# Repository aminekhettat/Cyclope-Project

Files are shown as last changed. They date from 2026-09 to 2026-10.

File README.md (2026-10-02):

# Cyclope

**A street-crossing assistant for blind and visually impaired people.**

The white cane tells you where to put your foot. GPS tells you where to go.
At the kerb, nothing speaks. Cyclope addresses that exact moment: recognising a
crosswalk, reading the state of a pedestrian traffic light, and guiding by voice
to a spoken address.

Developed by **[Blind Systems](https://www.blindsystems.org)** together with
successive cohorts of embedded-systems engineering students.

---

## Table of contents

- [About the project](#about-the-project)
- [Three generations](#three-generations)
- [Generation 3 architecture](#generation-3-architecture)
- [Repository layout](#repository-layout)
- [Getting started](#getting-started)
- [The four work packages](#the-four-work-packages)
- [Contributing](#contributing)
- [License and contact](#license-and-contact)

---

## About the project

Existing assistive devices — OrCam MyEye, Envision Glasses, Aira, Be My Eyes —
read text, describe scenes and recognise objects. None of them answers the two
questions that come up at every street corner: **where exactly is the crosswalk,
and is the light green for me?**

Cyclope deliberately limits itself to that problem. It is narrow enough to be
solved properly, rather than half-solved inside a device that claims to do
everything.

The project has three goals:

1. **On-device detection** of crosswalks and pedestrian traffic lights, with
   immediate voice feedback.
2. **Pedestrian navigation** guided by voice, from a spoken address.
3. **Map contribution**: report unmapped crosswalks to OpenStreetMap, after the
   user confirms by voice.

Cyclope is a research and development project. **It is not a product for sale,
and it does not replace the white cane.**

---

## Three generations

| | Period | Worn hardware | Where the intelligence runs | Limitation hit |
|---|---|---|---|---|
| **GEN 1** | 2024-2025 | 3D-printed glasses + ESP32-CAM; Raspberry Pi and battery in a backpack | Raspberry Pi, locally | Bulk: a computer carried on the back, a cable running down the face |
| **GEN 2** | 2025-2026 | 3D-printed glasses, board and battery in a central compartment | Remote AI service, reached through the phone over 4G | Dependence on a paid API, several seconds of latency |
| **GEN 3** | in progress | Two small enclosures clipped onto the temples of ordinary glasses | The user's own phone, offline | — |

### Generation 1 — the computer in the backpack

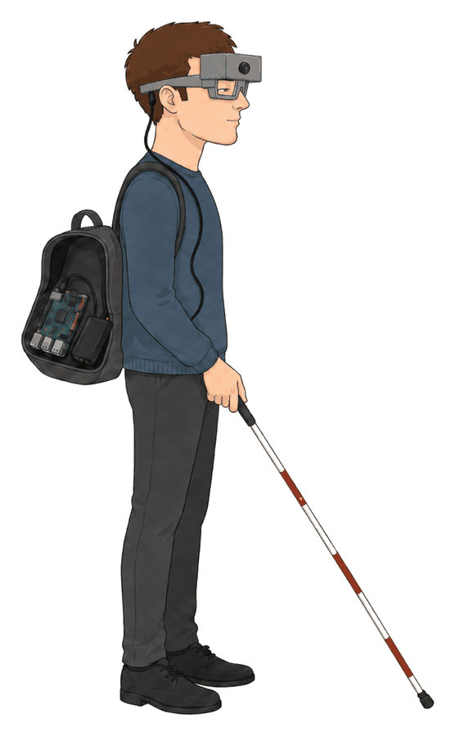
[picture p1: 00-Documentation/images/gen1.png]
Cartoon illustration of a blind man in profile holding a white cane. He wears bulky grey 3D-printed glasses with a large box on the forehead housing a camera. A black cable runs from the box down past his ear into an open backpack containing a green Raspberry Pi board and a battery.


An ESP32-CAM mounted on 3D-printed glasses streamed images over wifi to a
Raspberry Pi running the detection model. It worked — but the user had to carry a
computer and its battery on his back, with a cable hanging along his face.

### Generation 2 — the intelligence moved to the cloud

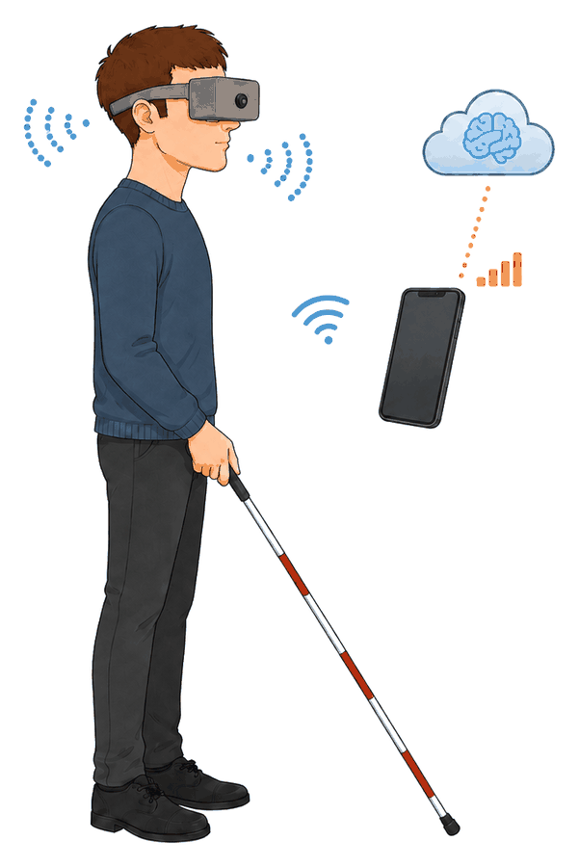
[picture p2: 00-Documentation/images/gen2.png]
Cartoon illustration of the same man. The backpack and cables are gone. A single 3D-printed box sits at the centre of the glasses frame, in front of the eyes. Blue wifi waves link the glasses to a smartphone; orange signal bars and a dotted line link the phone to a cloud symbol representing a remot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


The backpack disappeared: board and battery moved into a compartment built into
the glasses, and image analysis moved to a remote AI service reached through the
user's phone. Lighter to wear — but recognition now depended on a paid API and on
the mobile network, with several seconds of latency. Good enough to describe a
scene, not to warn in time.

### Generation 3 — computation moves back into the pocket

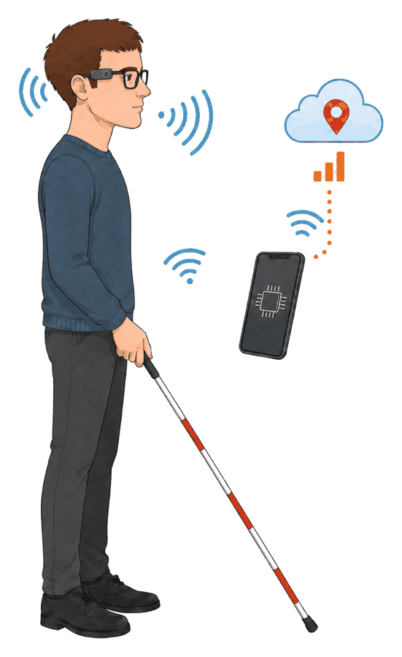
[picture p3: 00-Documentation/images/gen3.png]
Cartoon illustration of the same man wearing his own ordinary thin-framed glasses. A small industrial-looking module is clipped to each temple, joined by a thin cable running behind his head. Blue wifi waves link the module to a smartphone showing a processor chip icon; orange signal bars link the 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


The current version inverts the logic. The smartphone already in the user's
pocket becomes the brain: the detection model runs on it locally, offline and at
no cost. The network is only used for maps and addresses. On the hardware side we
stopped making glasses altogether — Cyclope is now a small module that clips onto
the user's own frames.

The common thread: **computation moves closer to the user, and cost tends
towards zero.**

Two lessons carried over from the previous generations:

- **We no longer build glasses.** Three runs of 3D-printed frames gave
  disappointing results in size, comfort and hinge robustness. GEN 3 clips onto
  the pair the person already chose.
- **We no longer depend on a remote AI for real-time detection.** Network latency
  is incompatible with an alert at the edge of a pavement.

---

## Generation 3 architecture

```
   Glasses module                  Android phone                   Internet
   ──────────────                  ─────────────                   ────────
   ESP32-S3 + camera   ── wifi ──▶  YOLO detection     ── 4G/5G ──▶  Nominatim
   2 buttons                        offline                          OSRM
   battery (2nd enclosure)          Voice feedback                   OpenStreetMap
                                    Navigation
```

- The **phone acts as the wifi access point**; the camera module connects to it
  as a client. No network setup is left to the user.
- **Visual detection runs offline**, on the phone.
- **Guidance requires an active data connection**: without internet, no address
  lookup and no route computation.
- **Voice feedback** is produced by the phone, which routes it to its own audio
  output (module speaker, wired or Bluetooth earphones).

GEN 3 hardware constraints: two enclosures joined by a USB-C cable running behind
the head, one holding the camera, the board and the buttons, the other the
battery, for balance. Mass target: **40 to 50 g**, with the OrCam MyEye 3 Pro
(22.5 g) as the market reference to keep in sight.

---

## Repository layout

This repository holds the whole project. It was assembled by merging the
historical per-topic repositories, **with full history and all branches
preserved**.

| Folder | Contents | Source repository |
|---|---|---|
| `00-Documentation/` | Cross-cutting documentation: meeting notes, specifications, reports | — |
| `01-Raspberry/` | GEN 1 server: stream reception, detection, recording | `Cyclope_Raspberry_Pi` |
| `02-Embedded/01-Software/` | ESP32 camera module firmware | `Cyclope_ESP32CAM` |
| `02-Embedded/02-Hardware/` | Schematic and PCB layout of the camera board | `Cyclope_ESP32CAM` |
| `03-Vision/` | YOLO model training, data augmentation, tests | `Cyclope_Vision` |
| `04-3D_Design/` | SolidWorks parts and STL files for the enclosures | `Cyclope-3D` |
| `05-MobilApp/` | Mobile applications: vision, navigation, voice feedback. `Android/` holds the current app, `iOS/` is reserved for a future port | `Cyclope_Androis` |

Folder numbering follows the chronological order of the project and fixes the
display order; it does not imply any dependency between work packages.

---

## Getting started

### Prerequisites per work package

| Package | Tools |
|---|---|
| `02-Embedded/01-Software` | ESP-IDF or Arduino IDE, ESP32-S3 board |
| `02-Embedded/02-Hardware` | **Altium Designer** (mandatory), parts verified as available at JLCPCB |
| `03-Vision` | Python 3.10+, Ultralytics, PyTorch |
| `04-3D_Design` | **SolidWorks** (mandatory) |
| `05-MobilApp/Android` | Android Studio, Kotlin, LiteRT |
| `05-MobilApp/iOS` | Xcode, Swift, Core ML - planned, not started |

### Clone

```bash
git clone https://github.com/ACCOUNT/Cyclope-Project.git
cd Cyclope-Project
```

### Train a detection model

```bash
cd 03-Vision
pip install -r requirements.txt      # create it if missing
python trainv11.py
```

### Large files: Git LFS

Model weights and CAD files are stored with **[Git LFS](https://git-lfs.com)**.
Install it once before cloning, otherwise those files arrive as small text
pointers instead of real content:

```bash
git lfs install
git clone https://github.com/ACCOUNT/Cyclope-Project.git
```

If you cloned before installing LFS, run `git lfs pull` to fetch the real files.

The following patterns are tracked, as recorded in the root `.gitattributes`:

```
*.pt  *.pth  *.onnx  *.tflite        model weights
*.STL  *.SLDPRT  *.SLDASM  *.SLDDRW  CAD parts and assemblies
```

Everything else — source code, documentation, images — stays in plain Git.

---

## The four work packages

GEN 3 is split into four independent subjects, each sized for **100 hours of one
student**. Every package can start immediately, without waiting for the others.

### 1. Electronics and enclosure — `02-Embedded/02-Hardware`, `04-3D_Design`

Adapt the existing GEN 2 schematic and redo the layout: replace the LDO with a
buck-boost converter, add at least two buttons, verify that every part is
available at JLCPCB. Design the two clip-on enclosures in SolidWorks. Assembly is
outsourced to JLCPCB: no soldering for the student. The ESP32-S3 is used as an
integrated module (antenna, SRAM, flash), which is out of scope for this project.

### 2. Embedded firmware — `02-Embedded/01-Software`

Image capture and compression, audio recording of voice commands (without
interpreting them), button handling, wifi link monitoring with a voice alert if
the connection drops.

### 3. Vision on Android — `05-MobilApp/Android`, `03-Vision`

Stream reception, on-device model inference, voice feedback. The student starts
with the already working DFRobot module from GEN 2, without waiting for the new
board.

### 4. Pedestrian navigation — `05-MobilApp/Android`

Spoken address input, geocoding through Nominatim, route computation, voice
guidance through TalkBack, positioning through the Fused Location and Fused
Orientation Providers. Includes the OpenStreetMap contribution feature. The
M5Stick C Plus serves as the button interface until the final module is ready.

---

## Contributing

### Branches

`main` is the reference branch and must always be in working order.

GEN 3 work takes place on the following branches, created from the current
`main` baseline. Each branch contains the complete repository; the work areas
below describe its purpose, not a restriction on which files can be edited.

| Branch | Work area |
|---|---|
| `CYCLOPE_GEN3_3D` | Clip-on enclosures, mechanical integration and SolidWorks files in `04-3D_Design/` |
| `CYCLOPE_GEN3_HW` | Schematics, PCB, power supply and buttons in `02-Embedded/02-Hardware/` |
| `CYCLOPE_GEN3_ESP32CAMSW` | ESP32-S3 camera firmware, audio capture, buttons and wifi in `02-Embedded/01-Software/` |
| `CYCLOPE_GEN3_AndroidVision` | Android stream reception, on-device detection and voice feedback in `05-MobilApp/Android/`, with model work in `03-Vision/` |
| `CYCLOPE_GEN3_AndroidNavigation` | Spoken destination, positioning, route guidance and OpenStreetMap contribution in `05-MobilApp/Android/` |

Collaborators may push commits to GEN 3 branches. Any additional work branch
must also start with `CYCLOPE_GEN3_`. Open a pull request to `main` when work is
ready for integration; the repository owner, `aminekhettat`, controls updates
to `main` and merges into it.

The historical branches (`android/…`, `design3d/…`, `embedded/…`, `raspberry/…`
and `vision/…`) are preserved as references. Collaborators cannot update or
delete them, or `main`. GitHub enforces this restriction on all branches outside
the `CYCLOPE_GEN3_` namespace, with bypass reserved to the repository admin.

The two Android branches share one application: coordinate interface changes
and integrate them through pull requests. The Raspberry Pi and future iOS port
have no dedicated GEN 3 work branch in the current scope.

### Commit messages

One imperative summary line, prefixed by the domain:

```
vision: add brightness-variation augmentation
embedded: fix wifi reconnection after access point loss
```

### Before pushing

- Never commit SolidWorks lock files (`~$…`), IDE settings (`.vs/`, `.idea/`) or
  build artefacts. The root `.gitignore` already excludes them.
- Large binary files must go through Git LFS. If you add a new binary type,
  register it first with `git lfs track "*.ext"` and commit the updated
  `.gitattributes` in the same change.

---

## License and contact

This project is released under the **Apache 2.0** license. See the `LICENSE` file.

- Website: [www.blindsystems.org](https://www.blindsystems.org)
- Contact: [contact@blindsystems.org](mailto:contact@blindsystems.org)

Field feedback — especially from blind and visually impaired users, occupational
therapists and orientation and mobility instructors — is what moves this project
forward the most.

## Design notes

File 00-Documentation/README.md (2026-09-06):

# Documentation

Cross-cutting documentation for the Cyclope project. One folder per work
package, mirroring the top-level layout of the repository.

| Folder | Holds |
|---|---|
| `Global/` | Documents covering the whole project: the presentation given to students, roadmaps, cross-package specifications |
| `01-Raspberry/` | Notes on the GEN 1 server |
| `02-Embedded/` | Meeting notes and specifications for the camera board and its firmware |
| `03-Vision/` | Dataset notes, training protocols, evaluation results |
| `04-3D_Design/` | Enclosure design notes, mass budget, print and assembly instructions |
| `05-MobilApp/` | Application specifications, accessibility notes, user-facing behaviour, one folder per platform |

`images/` holds the illustrations used by the root README.

Empty folders carry a `.gitkeep` file so that Git keeps them; delete it as
soon as the folder holds real content.

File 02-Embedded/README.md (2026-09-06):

# Cyclope_ESP32CAM
Repository that contain the PlatformIO project related to ESP32CAM modules management

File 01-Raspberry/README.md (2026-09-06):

# Cyclope_Raspberry_Pi
Repo that contains software development on Raspberry Pi that is used as a central calculation station

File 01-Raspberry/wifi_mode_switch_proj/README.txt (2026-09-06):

Voici comment installer et utiliser le script wifi_mode_switch.sh pour gérer le mode réseau de ton Raspberry Pi (mode Point d'accès ou mode Managed). 
Suis bien ces étapes :

Dans ton dossier de projet, tu devras avoir ces fichiers :

wifi_mode_switch.sh : Le script principal pour passer du mode AP au mode Managed.
hostapd.conf, dnsmasq.conf, dhcpcd.conf : Ces fichiers de configuration sont essentiels pour que le script fonctionne correctement.
install.sh : Un script qui copie automatiquement ces fichiers dans les répertoires système.

Il faudra également que tu modifies le fichier wpa_supplicant.conf ( je n'ai pas les droits pour le copier) qui se trouve dans /etc/wpa_supplicant.
Pour cela il faudra que tu tapes : 
sudo nano /etc/wpa_suppicant/wpa_supplicant.conf

et que tu rentres ces lignes de code : 

ctrl_interface=DIR=/var/run/wpa_supplicant GROUP=netdev
update_config=1

network={
    ssid="Nom_du_Réseau"   # Remplace par le SSID du réseau Wi-Fi
    psk="Mot_de_passe"      # Remplace par le mot de passe du réseau Wi-Fi
    key_mgmt=WPA2-PSK       # Utilise WPA2 pour la sécurité
}

Ouvre un terminal et va dans le dossier où tu as mis tous les fichiers (avec la commande cd). Ensuite, exécute le script install.sh en utilisant les droits administrateur pour que les fichiers de configuration soient copiés dans les bons répertoires système :

sudo ./install.sh
Ce script va :

Copier les fichiers de configuration (hostapd.conf, dnsmasq.conf, etc.) dans leurs répertoires respectifs sous /etc/.
Redémarrer les services nécessaires comme hostapd, dnsmasq, et dhcpcd pour appliquer la nouvelle configuration.

Une fois l’installation terminée, tu peux utiliser le script wifi_mode_switch.sh pour passer en mode Point d'accès ou Managed. Pour le faire, il suffit de passer l’argument approprié :

Pour passer en mode Point d'accès, lance cette commande :

sudo ./wifi_mode_switch.sh ap

Pour revenir en mode Managed, lance celle-ci :

sudo ./wifi_mode_switch.sh managed
Le script va automatiquement ajuster la configuration réseau de ton Raspberry Pi sans que tu aies à intervenir manuellement.

Si tu veux vérifier que ton Raspberry Pi est bien dans le mode que tu souhaites, tu peux utiliser des commandes comme ifconfig ou ip a pour voir l'état des interfaces réseau et leur configuration.

PS : Il se peut que lorsque tu exécutes la commande en mode AP, la raspberry reste en mode managed. Pour contrer cela, il te suffit de lancer la commande pour le mode managed et d'ensuite relancer la commande en AP.

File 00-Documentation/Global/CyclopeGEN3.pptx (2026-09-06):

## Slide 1

CyclopeGEN 3

Des lunettes qui disent où et quand traverser

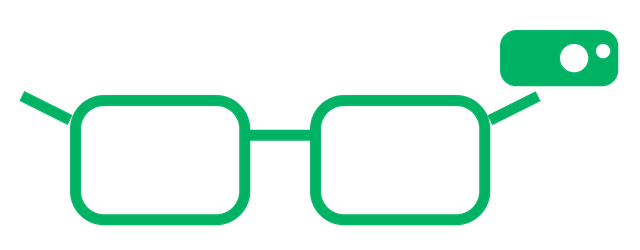
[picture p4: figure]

Projet longue durée · 5e année · Systèmes embarqués

Proposé par : Amine Khettat · BLIND SYSTEMS

E-mail : contact@blindsystems.org · www.blindsystems.org

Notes: 15 secondes. Une seule phrase : cette annee je vous propose la troisieme generation d'un projet qui tourne depuis deux ans, et cette annee c'est celle ou il devient portable.

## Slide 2

Le moment le plus dangereux est le moins outillé

La canne blanche dit où poser le pied.

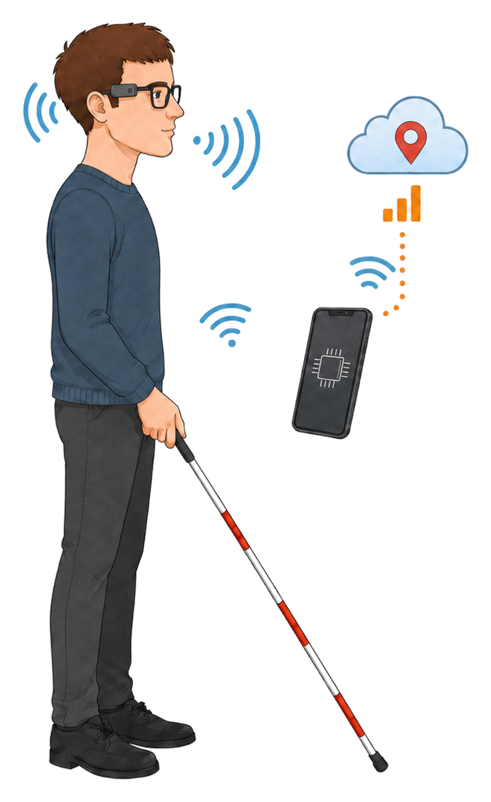
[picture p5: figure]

1

2

Le GPS dit où aller.

3

Rien, aujourd'hui, ne dit où ni quand traverser.

Cyclope regarde la rue et le dit à voix haute.

www.blindsystems.org · CyclopeGEN 3

2

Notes: 35 secondes. Insister sur le fait que traverser est le seul moment du trajet ou l'usager n'a aucune information. Ne pas parler d'obstacles : le sujet, c'est la traversee.

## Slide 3

1

GEN 1 — l'ordinateur dans le sac

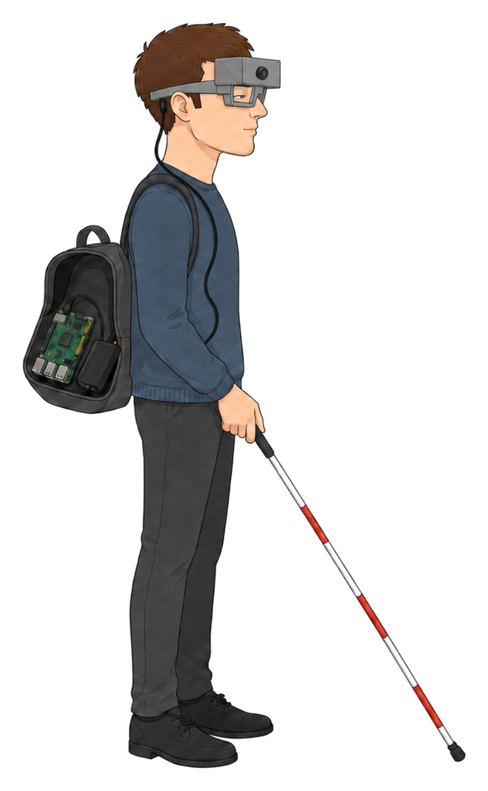
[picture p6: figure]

2024 – 2025

- Lunettes imprimées en 3D, branches non pliables, compartiment frontal abritant l'ESP32-CAM
- Câble d'alimentation apparent le long de l'oreille, jusqu'au sac à dos
- Raspberry Pi 5 et batterie dans le sac : flux MJPEG, YOLOv11, enregistrement vidéo
- Logique d'une caméra de sécurité que l'on porte sur soi

La limite

Des lunettes inconfortables, un câble qui pend, un sac à dos obligatoire.
Prototype lourd, non commercialisable.

Le calcul était dans un sac à dos. Il fallait l'en sortir.

www.blindsystems.org · CyclopeGEN 3

3

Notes: 30 secondes. La preuve de concept. Assumer l'echec franchement : c'est lui qui justifie la suite.

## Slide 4

2

GEN 2 — le serveur dans le cloud

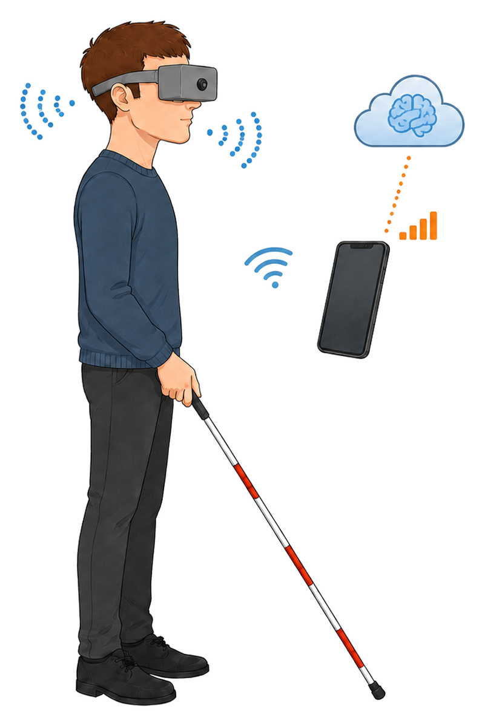
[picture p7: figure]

2025 – 2026

- Lunettes 3D avec un compartiment central devant les yeux : la carte et la batterie sont enfin embarquées
- Plus de Raspberry : l'ESP32 parle directement au téléphone, qui sert de point d'accès wifi
- Le téléphone relaie vers l'API d'OpenAI par sa 4G, et la scène est décrite à la voix
- En parallèle : carte DFRobot ESP32-S3, et conception de notre première carte maison

La limite

API payante, réseau obligatoire, quelques secondes de latence.
Le téléphone n'est qu'un relais : toute l'intelligence est ailleurs.

Le calcul était parti dans le cloud. Il fallait le rapatrier.

www.blindsystems.org · CyclopeGEN 3

4

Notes: 35 secondes. Le saut porte sur l'intelligence, pas sur le materiel. La limite de latence est ce qui amene GEN 3.

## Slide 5

3

GEN 3 — le téléphone déjà dans la poche

Module lunettes

Image, audio des commandes,
deux boutons

Téléphone

IA embarquée, hors ligne :
passages piétons, feux, couleur

Internet

Cartes et adresses seulement.
Aucune IA.

wifi local — le téléphone est le point d'accès

4G / 5G — sans données, pas de guidage

Deux boîtiers, un sur chaque branche

La batterie d'un côté, la caméra et la carte de l'autre, reliées par un fin câble d'alimentation : le poids est réparti et la monture reste en équilibre.
Cible 40 à 50 g — l'OrCam du marché en pèse 22,5.

On ne fabrique plus la lunette, on s'y accroche.

www.blindsystems.org · CyclopeGEN 3

5

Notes: 50 secondes. Deux messages : le calcul passe sur un telephone que l'usager a deja, et on arrete de fabriquer des lunettes. Preciser que la detection marche hors ligne, mais que le guidage exige une liaison de donnees. Les deux boitiers repondent au probleme d'equilibre de la monture. Insister : le telephone etait deja la en GEN 2, mais comme simple relais vers le cloud. En GEN 3 il devient le cerveau.

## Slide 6

Quatre briques, quatre élèves

Électronique et boîtiers

Adapter le schéma GEN 2, refaire le routage, buck-boost, deux boutons, et les deux boîtiers équilibrés sur les branches.

Altium · SolidWorks · JLCPCB

1

Firmware embarqué

Capture et compression d'image, enregistrement audio des commandes, gestion des appuis, surveillance du lien wifi.

ESP-IDF · C++ · ESP32-S3

2

Vision sur Android

Passages piétons, feux et leur couleur en temps réel, plus la description de scène à la demande, héritée de GEN 2.

YOLO · LiteRT · Kotlin

3

Navigation piétonne

Adresse dictée, itinéraire, guidage vocal, et contribution des passages manquants à OpenStreetMap.

Vosk · Nominatim · OSRM · TalkBack

4

Interfaces figées avant le démarrage, et un substitut pour chaque dépendance : personne n'attend personne.

www.blindsystems.org · CyclopeGEN 3

6

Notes: 80 secondes, la slide pivot. Une phrase par brique, pas plus. Terminer sur les substituts : la vision et le firmware demarrent sur les cartes DFRobot, la navigation sur le M5Stick. Aucun eleve n'est bloque par un autre.

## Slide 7

Le cadre

100 h

par élève

2

cartes prêtes à l'emploi

0

composant à braser

- Un dépôt git unique : une branche de travail par brique, modules Gradle séparés côté Android
- Matériel disponible dès la première séance, assemblage de la carte sous-traité
- Que du logiciel libre et gratuit, aucun abonnement
- Livrables : une démonstration qui fonctionne, et la documentation qui va avec

La démonstration de fin d'année est garantie : le système complet tourne déjà sur le matériel GEN 2.

www.blindsystems.org · CyclopeGEN 3

7

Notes: 25 secondes. Le message qui leve les freins : le materiel est la, rien a braser, et la demo finale ne depend pas de la nouvelle carte.

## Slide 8

Pourquoi celui-là

Un projet dont quelqu'un se servira vraiment

La chaîne complète : capteur, IA embarquée, utilisateur

Une démonstration que vous pourrez montrer, et garder

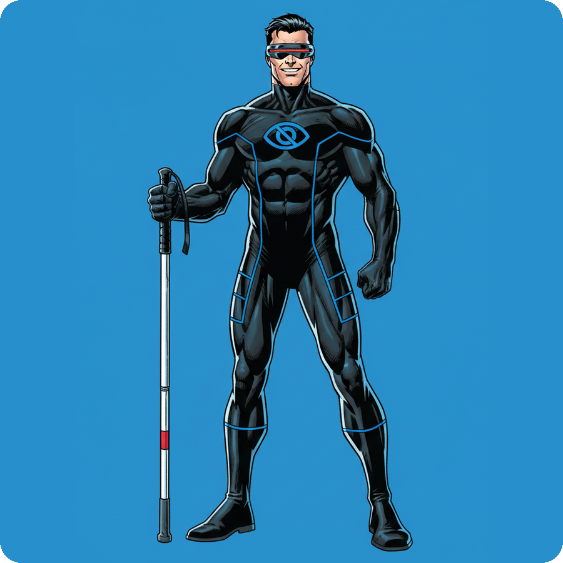
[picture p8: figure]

Venez me voir à la fin de la séance.

Proposé par : Amine Khettat · BLIND SYSTEMS

E-mail : contact@blindsystems.org · www.blindsystems.org

www.blindsystems.org · CyclopeGEN 3

8

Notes: 15 secondes. Terminer sur l'invitation, pas sur la technique.

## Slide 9

Annexe — jeux de données et versions de YOLO

Jeux de données utilisables directement

- CDSet / CDNet — passages piétons : 3 080 images d'entraînement, 1 770 de test, annotations déjà au format YOLO, deux classes (passage, flèche au sol)
- PTL / ImVisible — feux piétons : 5 059 images, cinq classes dont vert avec décompte, licence MIT ; le réseau LytNet tourne à 21 images/s sur un iPhone 7
- Ampel-Pilot — feux piétons allemands : 3 696 images, 4 311 annotations, licence MIT, collecté pour une application destinée aux malvoyants
- Et le jeu de données Cyclope 2024-2025, déjà constitué et augmenté par la promotion GEN 1

Attention : Bosch, LISA et DriveU sont des jeux de feux véhicules vus depuis une voiture. Cyclope a besoin de feux piétons vus du trottoir — autre objet, autre point de vue.

Versions de YOLO

- YOLOv5 : celui de CDNet, le seul si l'on veut réutiliser des poids existants tels quels — YOLOv8 puis YOLO11, celui déjà entraîné en GEN 1 : écosystème mature
- YOLO26 (janvier 2026) : inférence sans NMS, donc plus de post-traitement à réimplémenter sur mobile, environ 43 % plus rapide sur CPU, export LiteRT
- Licence AGPL-3.0 pour tous les modèles Ultralytics ; YOLOX est en Apache 2.0 si une exploitation commerciale est envisagée un jour

www.blindsystems.org · CyclopeGEN 3

9

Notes: Annexe, hors chrono. A sortir si un eleve demande sur quoi il va entrainer son modele.

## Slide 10

Annexe — le contrat d'interface

Le sens de la liaison wifi

Le téléphone active son point d'accès, le module s'y connecte. La 4G reste la route internet du téléphone : aucun conflit de réseau.

Ce que porte le protocole

Trames JPEG, audio des commandes vocales, événements bouton, état du lien. Figé avant le démarrage, identique pour le M5Stick et pour la carte finale.

Le retour vocal

L'application envoie une commande de lecture au téléphone, qui route vers sa sortie — haut-parleur, écouteurs filaires ou Bluetooth. Hors périmètre du projet.

Deux liens surveillés, deux alertes

Le firmware surveille le wifi et alerte sur son propre haut-parleur, seul cas où le téléphone ne peut plus parler. L'application surveille la liaison de données.

Les substituts

Vision et firmware démarrent sur les deux cartes DFRobot de GEN 2, la navigation sur le M5Stick C Plus, lui aussi en wifi. Aucune brique n'attend une autre.

Question ouverte à traiter dès la conception : comment le module apprend-il le nom et le mot de passe du point d'accès, sans écran ni clavier ?

www.blindsystems.org · CyclopeGEN 3

10

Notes: Annexe, hors chrono. A sortir si un eleve demande comment les briques communiquent.

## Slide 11

Annexe — l'état de l'art

Un boîtier qui se clipse sur la monture de lunettes. Lit le texte à voix haute, reconnaît visages et objets, traitement embarqué. C'est notre référence de format et de poids.

OrCam MyEye

Envision Glasses

Des lunettes connectées : lecture de texte, description de scène, appel à un proche voyant. Orientées lecture et reconnaissance.

eSight

Des lunettes à écrans internes qui amplifient et retraitent l'image. Conçues pour la vision résiduelle, donc pas pour les non-voyants.

Aira

Un service d'agents humains formés, joignables depuis l'application, qui décrivent la scène en direct par la caméra. Sur abonnement.

Be My Eyes

Une application gratuite qui met en relation avec des bénévoles voyants, doublée d'une description automatique par IA.

Rango, de GoSense

Un boîtier français qui se clipse sur la canne blanche : détection d'obstacles et guidage sonore, avec dictée d'adresse. Le plus proche de nous.

Aucun des six ne traite la traversée de rue : ni où traverser, ni quand. C'est précisément là que Cyclope se place.

www.blindsystems.org · CyclopeGEN 3

11

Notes: Annexe, hors chrono. Le benchmark vient du rapport GEN 1. Le point a retenir : tous lisent du texte ou decrivent une scene, aucun ne repond a la question de la traversee.

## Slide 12

Annexe — références

- CDSet, jeu de données passages piétons — zenodo.org/records/8289874
- CDNet, détection de passages piétons temps réel — github.com/zhangzhengde0225/CDNet
- ImVisible et LytNet, feux piétons pour malvoyants — github.com/samuelyu2002/ImVisible
- Ampel-Pilot, feux piétons allemands — github.com/patVlnta/Ampel-Pilot-Dataset
- Ultralytics YOLO26 — docs.ultralytics.com/models/yolo26
- monicz.dev — cartographie automatique de passages piétons sur OpenStreetMap
- OrCam MyEye 3 Pro — 22,5 g, 76 × 21 × 14,9 mm, fixation magnétique sur la branche
- Rango, de GoSense (Lyon) — la référence française du guidage pour non-voyants

www.blindsystems.org · CyclopeGEN 3

12

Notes: Annexe, hors chrono.

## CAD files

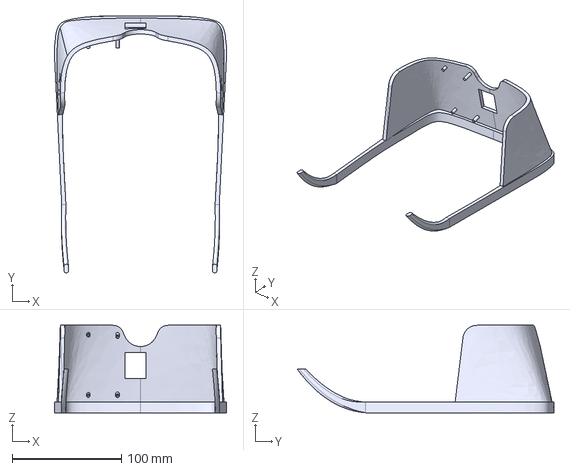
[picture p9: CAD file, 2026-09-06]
02-Embedded/02-Hardware/Glasses_ISMAIL.step
157.3 x 234.9 x 80.0 mm

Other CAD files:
04-3D_Design/Assemblage_lunettes - Lunettes-1.STL
04-3D_Design/Assemblage_lunettes - Boitier-2.STL
04-3D_Design/Assemblage_lunettes.SLDASM
04-3D_Design/Lunettes.SLDPRT
04-3D_Design/Boitier.SLDPRT

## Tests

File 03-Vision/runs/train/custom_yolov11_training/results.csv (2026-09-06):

epoch | time | train/box_loss | train/cls_loss | train/dfl_loss | metrics/precision(B) | metrics/recall(B) | metrics/mAP50(B) | metrics/mAP50-95(B) | val/box_loss | val/cls_loss | val/dfl_loss | lr/pg0 | lr/pg1 | lr/pg2
1 | 111.023 | 1.40003 | 2.88625 | 1.55938 | 0.51152 | 0.40126 | 0.38823 | 0.22607 | 1.52438 | 1.95877 | 1.66085 | 0.00033223 | 0.00033223 | 0.00033223
2 | 226.436 | 1.35667 | 1.93575 | 1.5003 | 0.5898 | 0.48392 | 0.46685 | 0.26641 | 1.55463 | 1.6891 | 1.64722 | 0.000652385 | 0.000652385 | 0.000652385
3 | 339.31 | 1.32899 | 1.60861 | 1.46598 | 0.57497 | 0.4881 | 0.49652 | 0.27497 | 1.63236 | 1.5564 | 1.78132 | 0.00095934 | 0.00095934 | 0.00095934
4 | 452.086 | 1.31024 | 1.44595 | 1.44707 | 0.68048 | 0.53559 | 0.5746 | 0.32416 | 1.55523 | 1.44 | 1.62224 | 0.0009406 | 0.0009406 | 0.0009406
5 | 572.982 | 1.25822 | 1.31063 | 1.40136 | 0.69185 | 0.52315 | 0.55078 | 0.34459 | 1.38886 | 1.31957 | 1.51859 | 0.0009208 | 0.0009208 | 0.0009208
6 | 694.308 | 1.22613 | 1.2392 | 1.37718 | 0.72523 | 0.57857 | 0.60999 | 0.36042 | 1.42285 | 1.2142 | 1.52768 | 0.000901 | 0.000901 | 0.000901
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

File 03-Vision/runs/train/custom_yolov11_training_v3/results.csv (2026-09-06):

epoch | time | train/box_loss | train/cls_loss | train/dfl_loss | metrics/precision(B) | metrics/recall(B) | metrics/mAP50(B) | metrics/mAP50-95(B) | val/box_loss | val/cls_loss | val/dfl_loss | lr/pg0 | lr/pg1 | lr/pg2
1 | 175.57 | 1.30136 | 2.04895 | 1.51353 | 0.63001 | 0.55663 | 0.5529 | 0.34393 | 1.40303 | 1.48832 | 1.51691 | 0.0033223 | 0.0033223 | 0.0033223
2 | 356.928 | 1.2394 | 1.30434 | 1.42803 | 0.68141 | 0.51924 | 0.57533 | 0.3374 | 1.48535 | 1.28497 | 1.66132 | 0.00663916 | 0.00663916 | 0.00663916
3 | 536.09 | 1.2954 | 1.29864 | 1.45799 | 0.66905 | 0.55345 | 0.57695 | 0.35933 | 1.40399 | 1.59334 | 1.62224 | 0.00993952 | 0.00993952 | 0.00993952
4 | 714.9 | 1.33262 | 1.31706 | 1.47529 | 0.70626 | 0.54789 | 0.58106 | 0.3503 | 1.42574 | 1.39348 | 1.62697 | 0.00992575 | 0.00992575 | 0.00992575
5 | 893.806 | 1.2869 | 1.21493 | 1.44021 | 0.82373 | 0.56077 | 0.64449 | 0.38767 | 1.42394 | 1.28836 | 1.54035 | 0.009901 | 0.009901 | 0.009901
6 | 1072.63 | 1.24432 | 1.15244 | 1.40564 | 0.82418 | 0.58405 | 0.66179 | 0.41749 | 1.2629 | 1.1314 | 1.44526 | 0.00987625 | 0.00987625 | 0.00987625
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

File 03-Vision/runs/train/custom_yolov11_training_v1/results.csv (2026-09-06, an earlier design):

epoch | time | train/box_loss | train/cls_loss | train/dfl_loss | metrics/precision(B) | metrics/recall(B) | metrics/mAP50(B) | metrics/mAP50-95(B) | val/box_loss | val/cls_loss | val/dfl_loss | lr/pg0 | lr/pg1 | lr/pg2
1 | 106.874 | 1.39041 | 3.20715 | 1.55206 | 0.37403 | 0.33083 | 0.33184 | 0.19432 | 1.51314 | 2.13887 | 1.57352 | 0.0033223 | 0.0033223 | 0.0033223
2 | 211.66 | 1.36292 | 2.19266 | 1.49892 | 0.59674 | 0.42867 | 0.45815 | 0.27465 | 1.45736 | 1.84805 | 1.58135 | 0.00663916 | 0.00663916 | 0.00663916
3 | 317.653 | 1.3674 | 1.88557 | 1.4937 | 0.5968 | 0.44064 | 0.45027 | 0.24702 | 1.65117 | 1.74711 | 1.77154 | 0.00993952 | 0.00993952 | 0.00993952
4 | 423.304 | 1.40957 | 1.7112 | 1.52288 | 0.64386 | 0.49048 | 0.50128 | 0.28947 | 1.51609 | 1.53231 | 1.66534 | 0.00992575 | 0.00992575 | 0.00992575
5 | 529.312 | 1.36471 | 1.51135 | 1.47739 | 0.76575 | 0.50121 | 0.57192 | 0.32437 | 1.49757 | 1.45249 | 1.60595 | 0.009901 | 0.009901 | 0.009901
6 | 636.017 | 1.33 | 1.40148 | 1.45757 | 0.68481 | 0.528 | 0.5604 | 0.33133 | 1.48398 | 1.38946 | 1.61082 | 0.00987625 | 0.00987625 | 0.00987625
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

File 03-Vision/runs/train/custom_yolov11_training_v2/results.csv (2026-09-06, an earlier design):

epoch | time | train/box_loss | train/cls_loss | train/dfl_loss | metrics/precision(B) | metrics/recall(B) | metrics/mAP50(B) | metrics/mAP50-95(B) | val/box_loss | val/cls_loss | val/dfl_loss | lr/pg0 | lr/pg1 | lr/pg2
1 | 123.104 | 1.34903 | 2.2515 | 1.53528 | 0.59989 | 0.48032 | 0.50617 | 0.30305 | 1.4329 | 1.32398 | 1.54411 | 0.0033223 | 0.0033223 | 0.0033223
2 | 249.056 | 1.25739 | 1.33016 | 1.4187 | 0.64755 | 0.50792 | 0.56872 | 0.35444 | 1.36075 | 1.39602 | 1.45911 | 0.00663916 | 0.00663916 | 0.00663916
3 | 378.102 | 1.30145 | 1.2859 | 1.43846 | 0.56419 | 0.53386 | 0.52213 | 0.30159 | 1.46114 | 1.43889 | 1.65279 | 0.00993952 | 0.00993952 | 0.00993952
4 | 507.061 | 1.34837 | 1.31839 | 1.46878 | 0.6467 | 0.53136 | 0.54582 | 0.3342 | 1.49357 | 1.46021 | 1.65333 | 0.00992575 | 0.00992575 | 0.00992575
5 | 636.223 | 1.30388 | 1.24159 | 1.42851 | 0.69306 | 0.53522 | 0.56421 | 0.32341 | 1.49617 | 1.36799 | 1.5882 | 0.009901 | 0.009901 | 0.009901
6 | 766.093 | 1.2745 | 1.16205 | 1.40862 | 0.73019 | 0.57636 | 0.61628 | 0.37205 | 1.36011 | 1.23116 | 1.51743 | 0.00987625 | 0.00987625 | 0.00987625
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

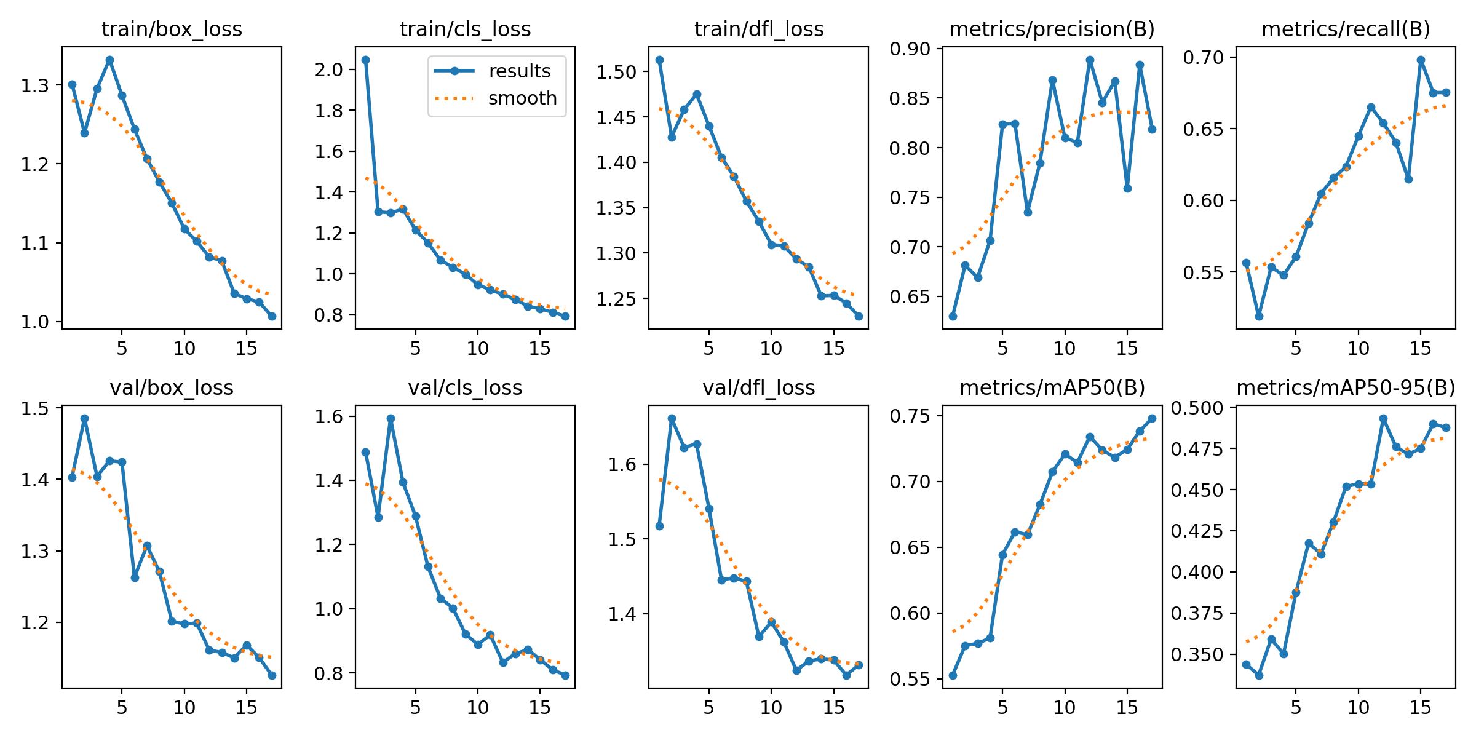
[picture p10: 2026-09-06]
03-Vision/runs/train/custom_yolov11_training_v3/results.png

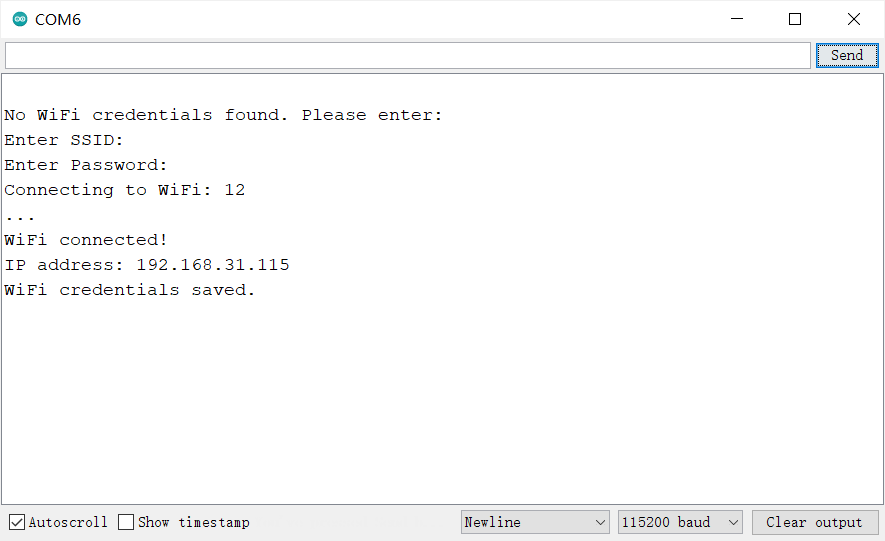
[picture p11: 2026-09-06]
02-Embedded/01-Software/ESP32Cam/PCB_firmware/CameraWebServer/Result.png

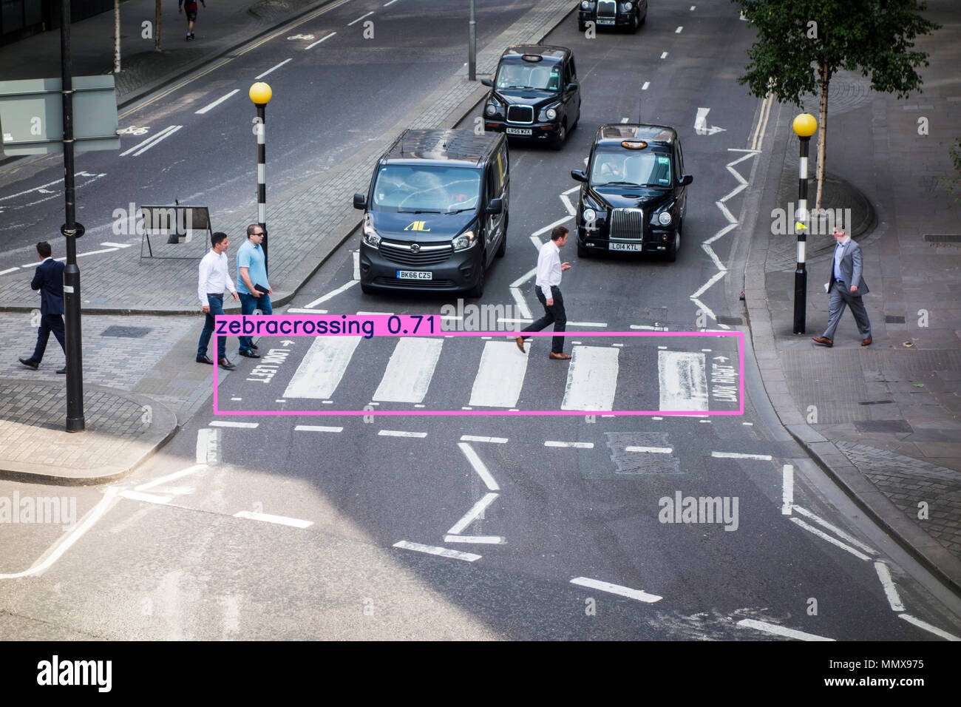
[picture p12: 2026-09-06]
03-Vision/result_initial.jpg

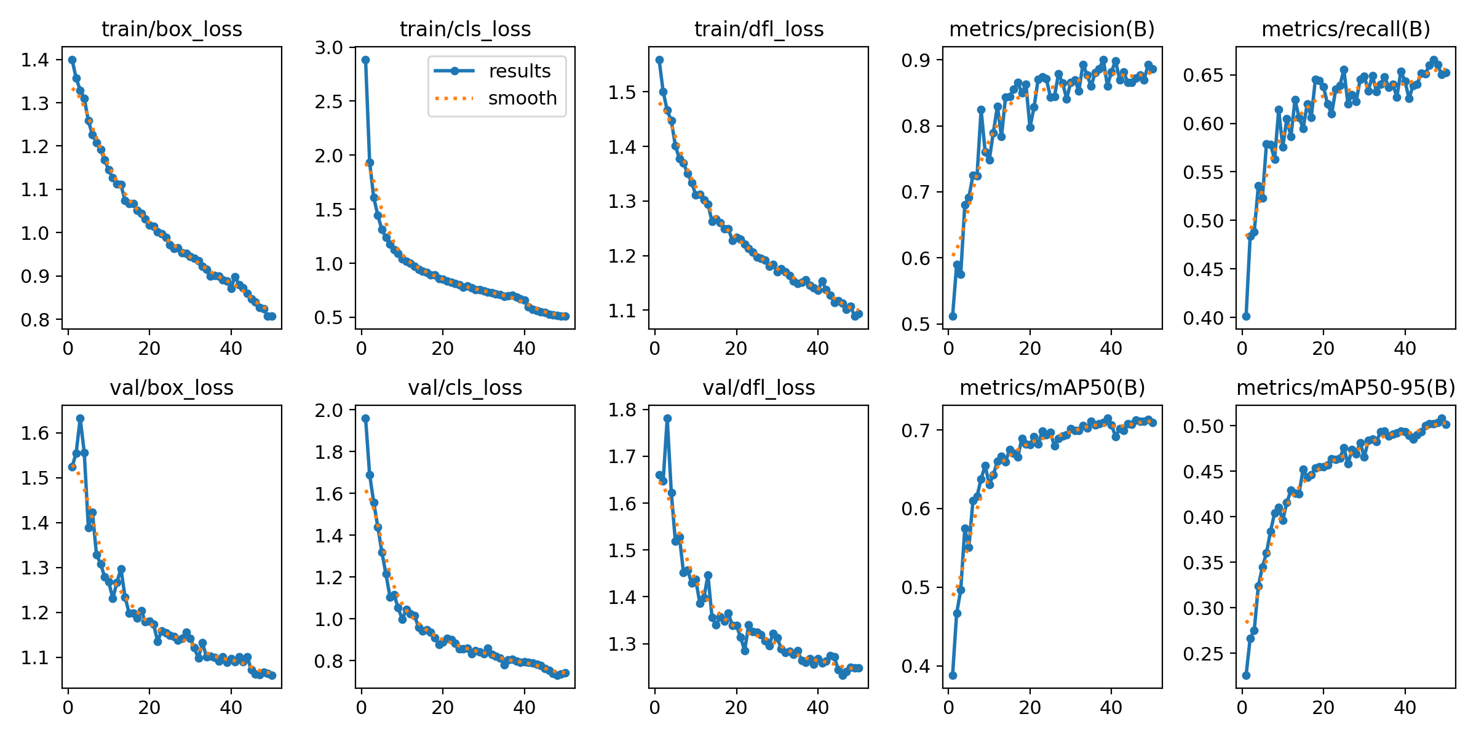
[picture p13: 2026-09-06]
03-Vision/runs/train/custom_yolov11_training/results.png

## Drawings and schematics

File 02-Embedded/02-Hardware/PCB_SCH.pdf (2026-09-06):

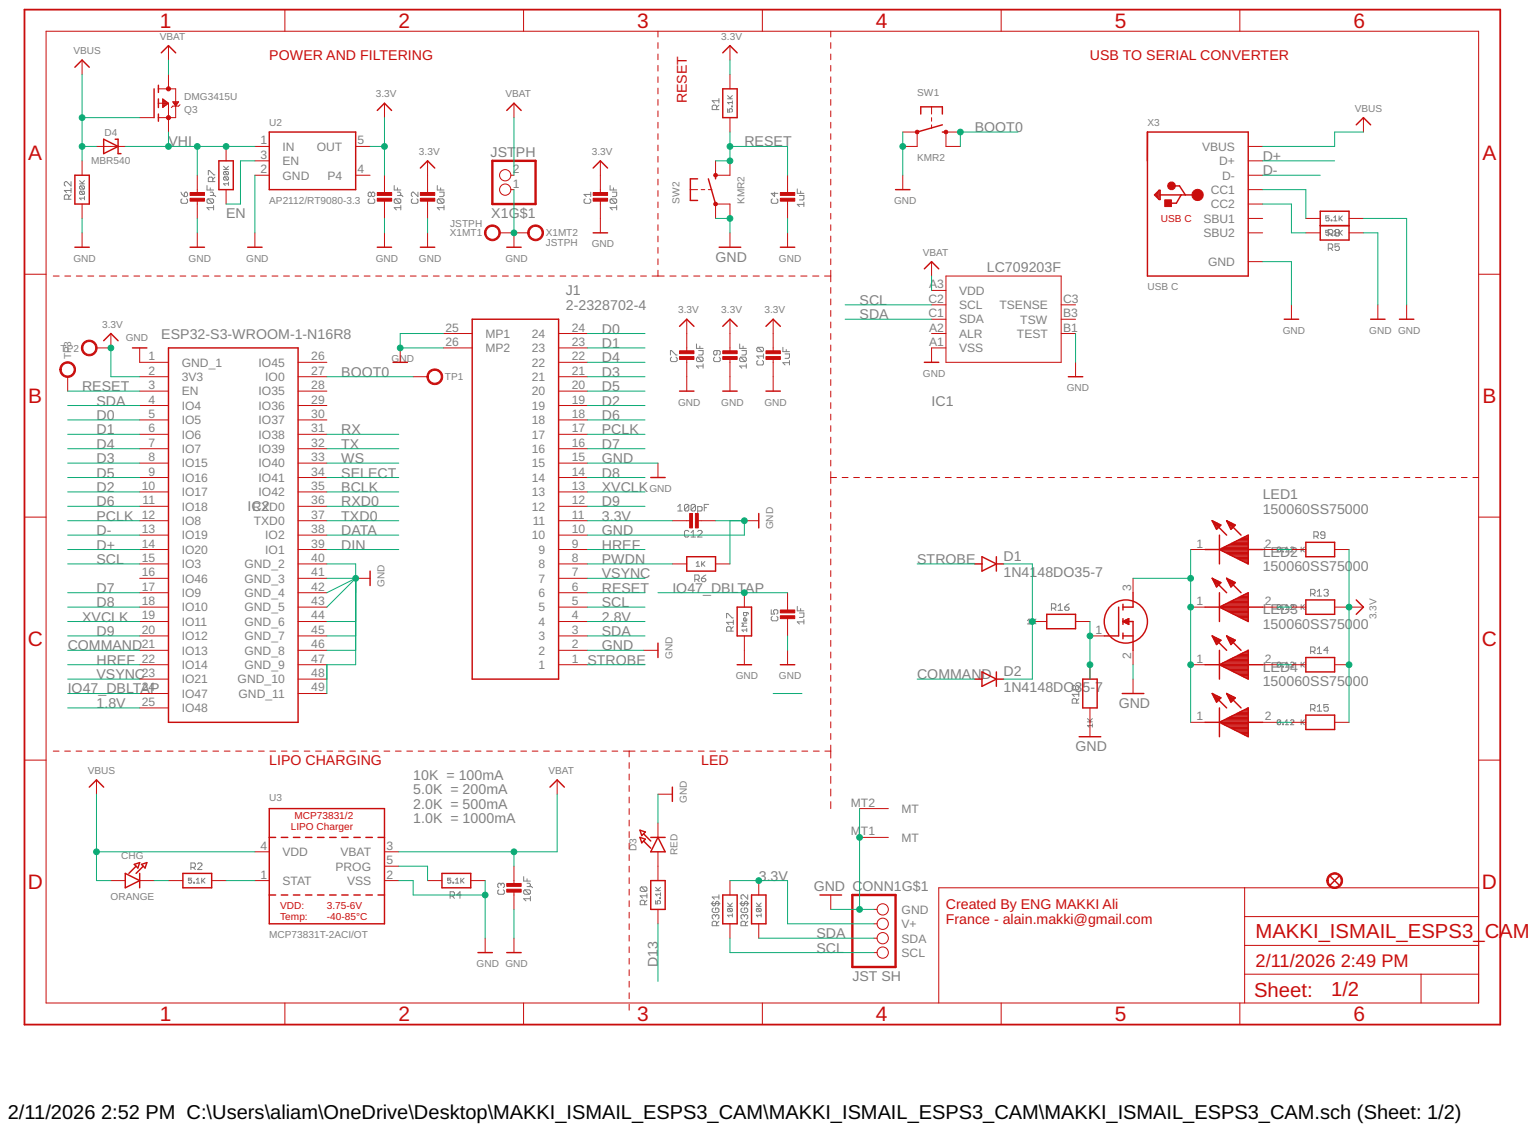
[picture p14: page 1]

VBAT | 3.3V

USB TO SERIAL CONVERTER

Created By ENG MAKKI Ali France - alain.makki@gmail.com

Sheet: 1/2

2/11/2026 2:52 PM C:\Users\aliam\OneDrive\Desktop\MAKKI_ISMAIL_ESPS3_CAM\MAKKI_ISMAIL_ESPS3_CAM\MAKKI_ISMAIL_ESPS3_CAM.sch (Sheet: 1/2)

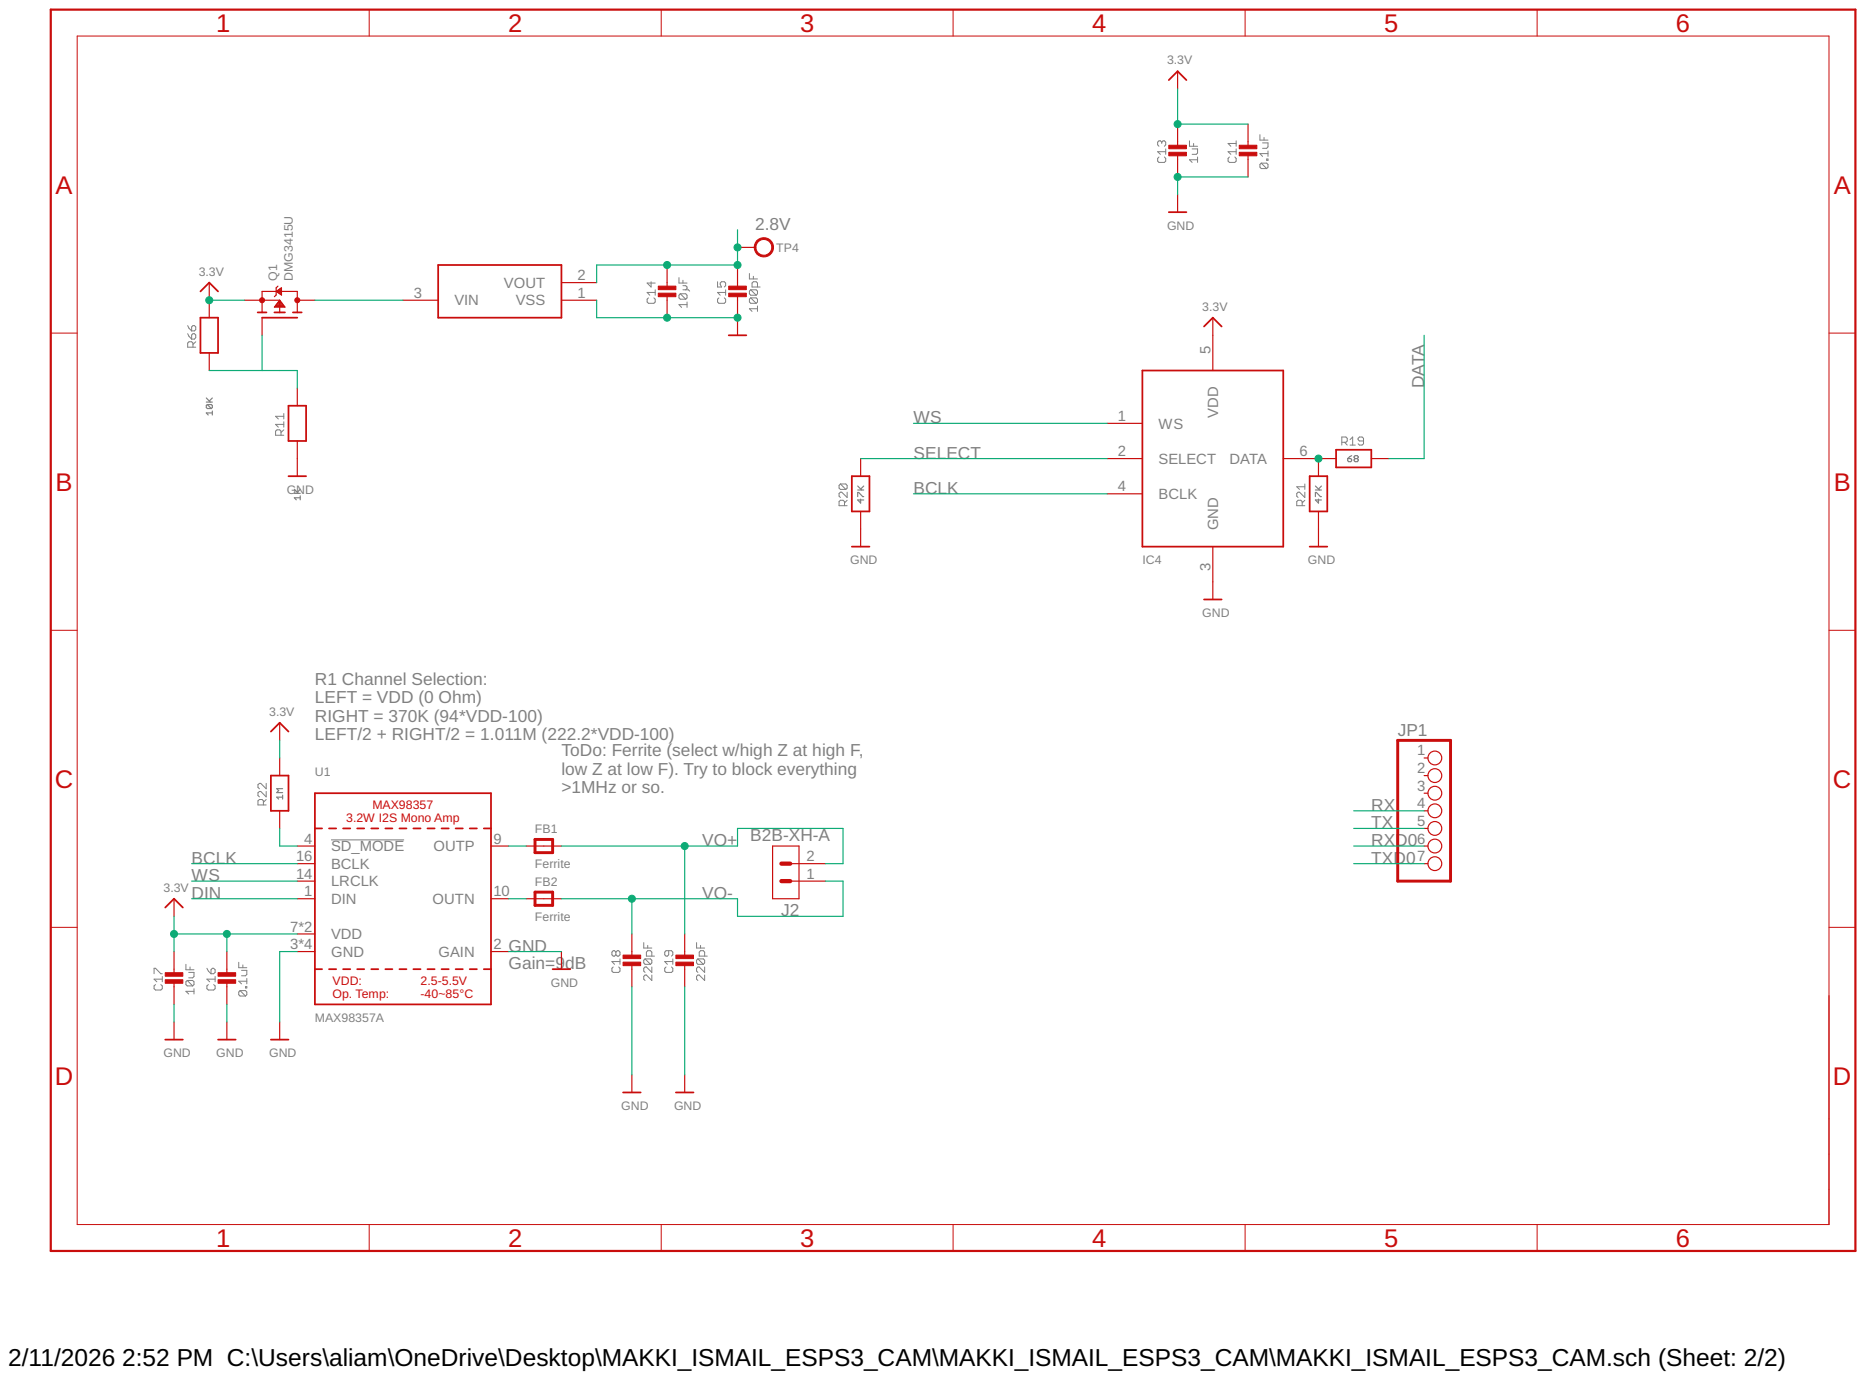
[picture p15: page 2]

R1 Channel Selection: LEFT = VDD (0 Ohm)

ToDo: Ferrite (select w/high Z at high F,
low Z at low F). Try to block everything >1MHz or so.

2/11/2026 2:52 PM C:\Users\aliam\OneDrive\Desktop\MAKKI_ISMAIL_ESPS3_CAM\MAKKI_ISMAIL_ESPS3_CAM\MAKKI_ISMAIL_ESPS3_CAM.sch (Sheet: 2/2)

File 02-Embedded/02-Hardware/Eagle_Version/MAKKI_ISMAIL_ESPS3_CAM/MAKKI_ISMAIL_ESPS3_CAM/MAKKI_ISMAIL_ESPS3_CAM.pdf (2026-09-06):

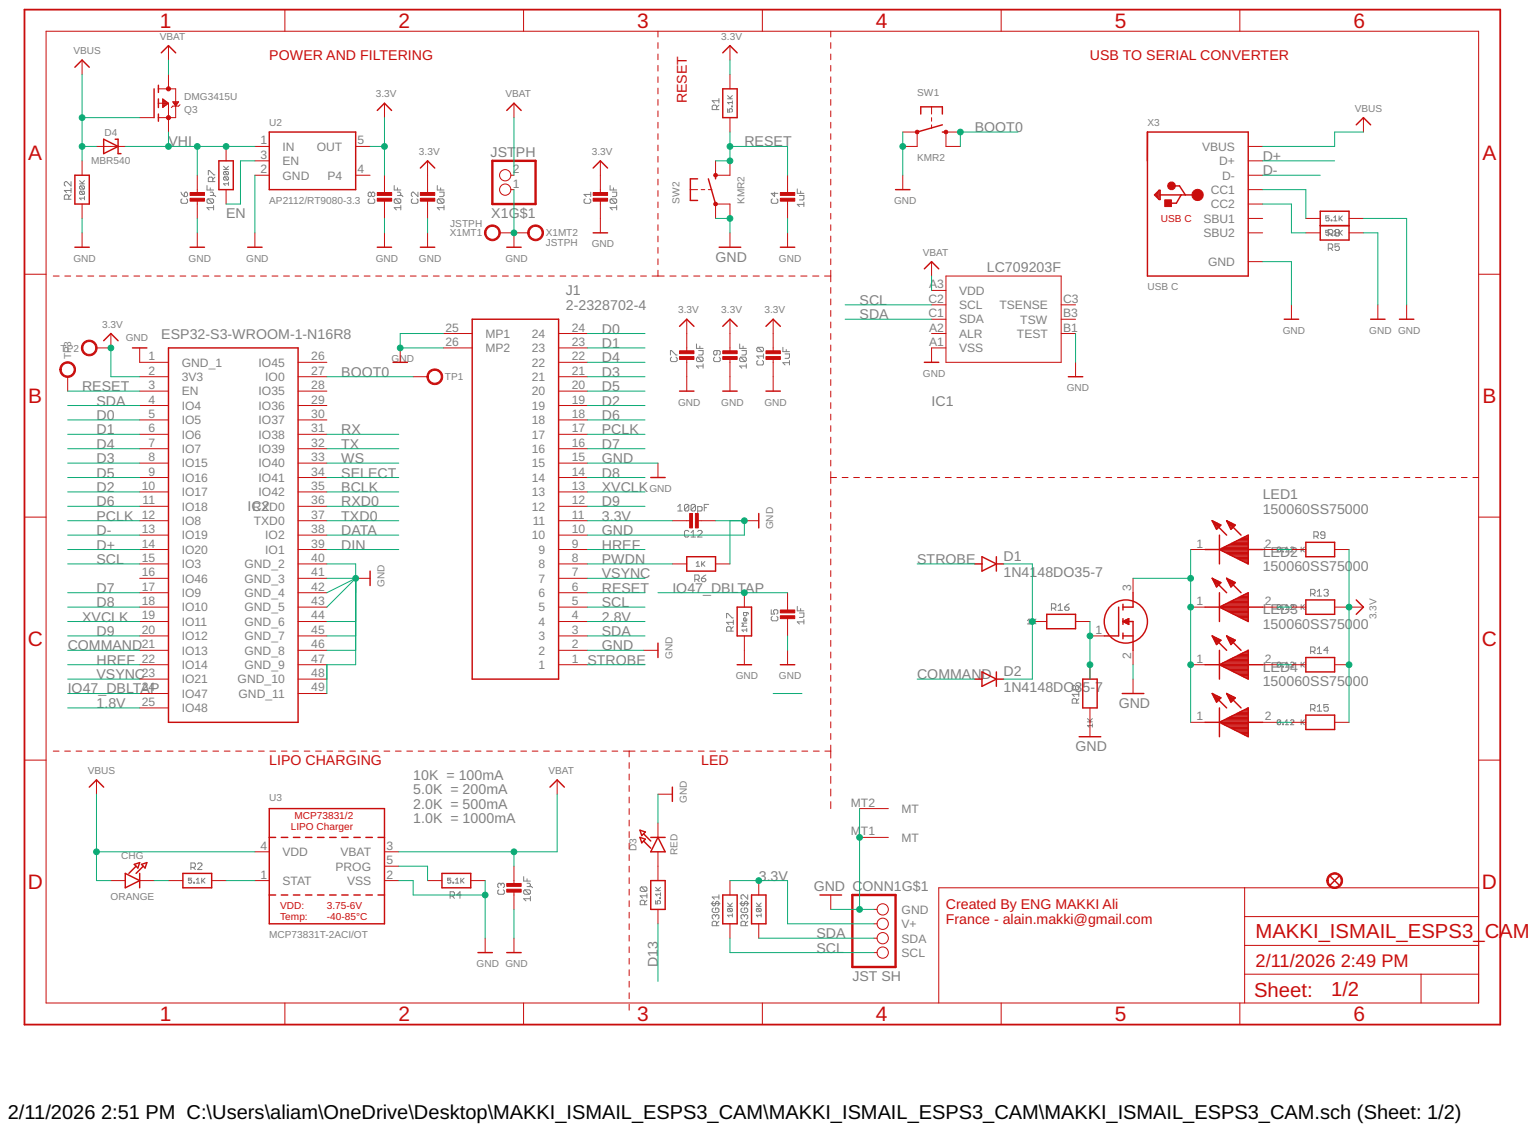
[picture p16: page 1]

VBAT | 3.3V

USB TO SERIAL CONVERTER

Created By ENG MAKKI Ali France - alain.makki@gmail.com

Sheet: 1/2

2/11/2026 2:51 PM C:\Users\aliam\OneDrive\Desktop\MAKKI_ISMAIL_ESPS3_CAM\MAKKI_ISMAIL_ESPS3_CAM\MAKKI_ISMAIL_ESPS3_CAM.sch (Sheet: 1/2)

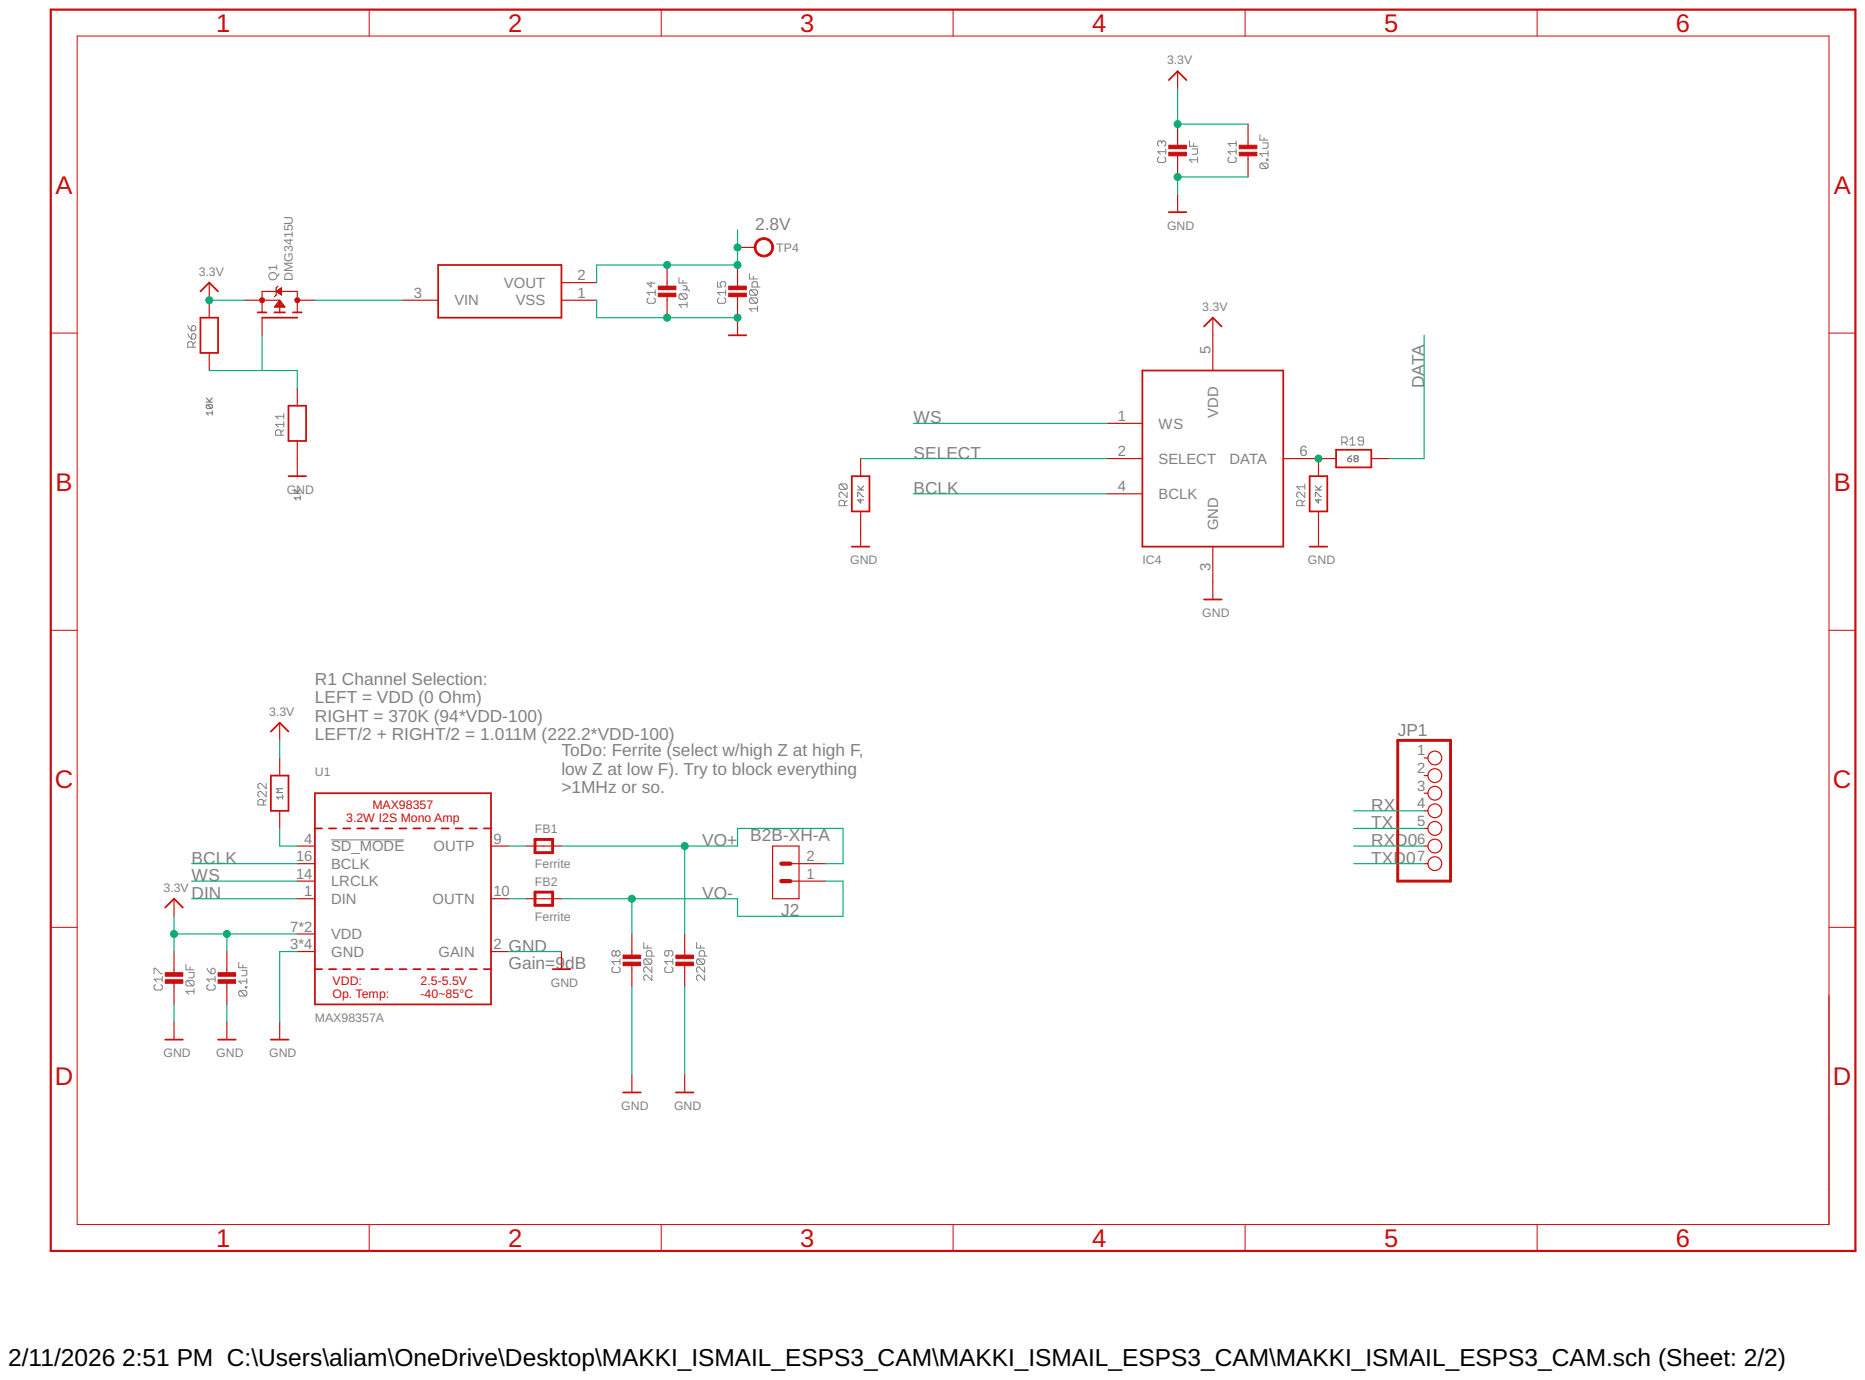
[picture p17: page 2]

R1 Channel Selection: LEFT = VDD (0 Ohm)

ToDo: Ferrite (select w/high Z at high F,
low Z at low F). Try to block everything >1MHz or so.

2/11/2026 2:51 PM C:\Users\aliam\OneDrive\Desktop\MAKKI_ISMAIL_ESPS3_CAM\MAKKI_ISMAIL_ESPS3_CAM\MAKKI_ISMAIL_ESPS3_CAM.sch (Sheet: 2/2)

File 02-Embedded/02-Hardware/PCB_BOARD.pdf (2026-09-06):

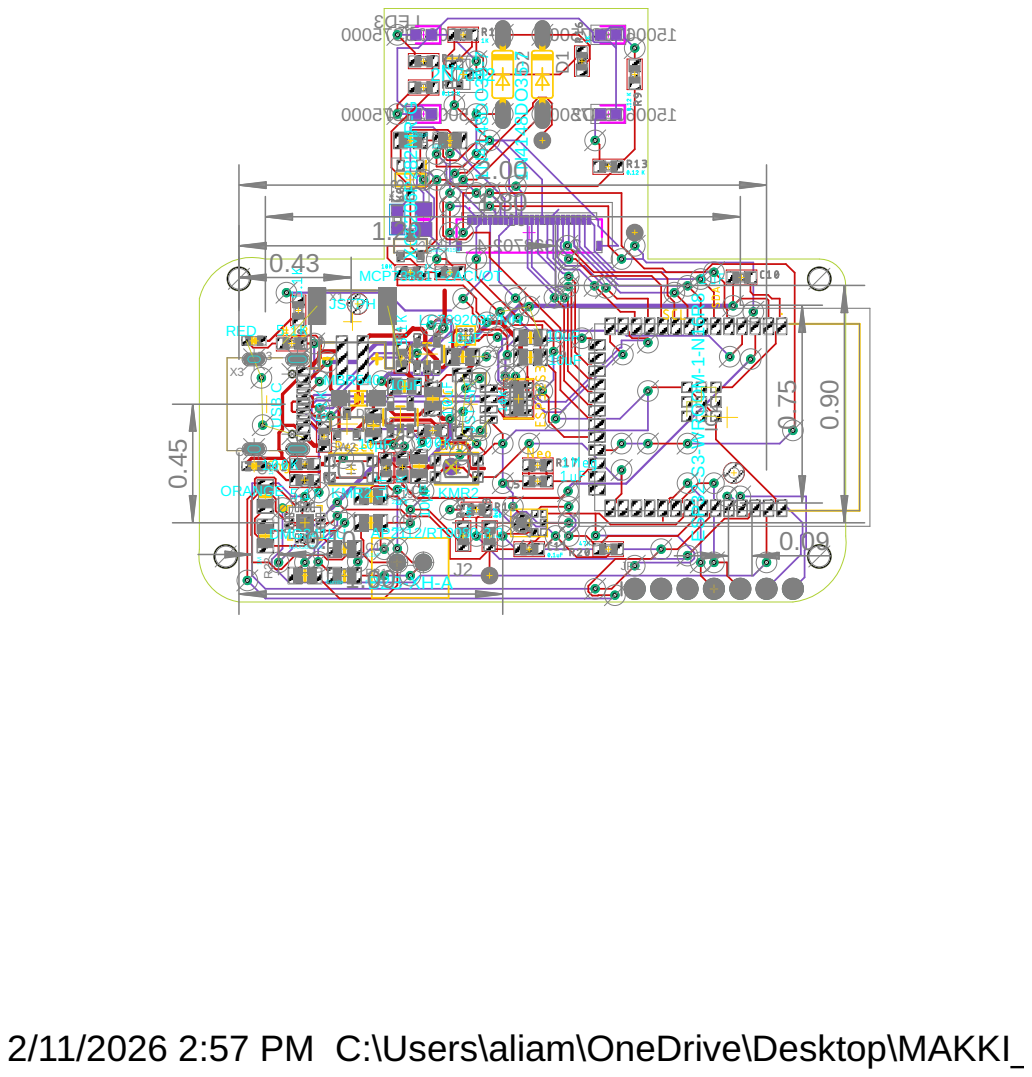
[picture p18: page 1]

DMG3415U | MAX98357A | 0.1uF

2/11/2026 2:57 PM C:\Users\aliam\OneDrive\Desktop\MAKKI_ISMAIL_ESPS3_CAM\MAKKI_ISMAIL_ESPS3_CAM\MAKKI_ISMAIL_ESPS3_CAM.brd

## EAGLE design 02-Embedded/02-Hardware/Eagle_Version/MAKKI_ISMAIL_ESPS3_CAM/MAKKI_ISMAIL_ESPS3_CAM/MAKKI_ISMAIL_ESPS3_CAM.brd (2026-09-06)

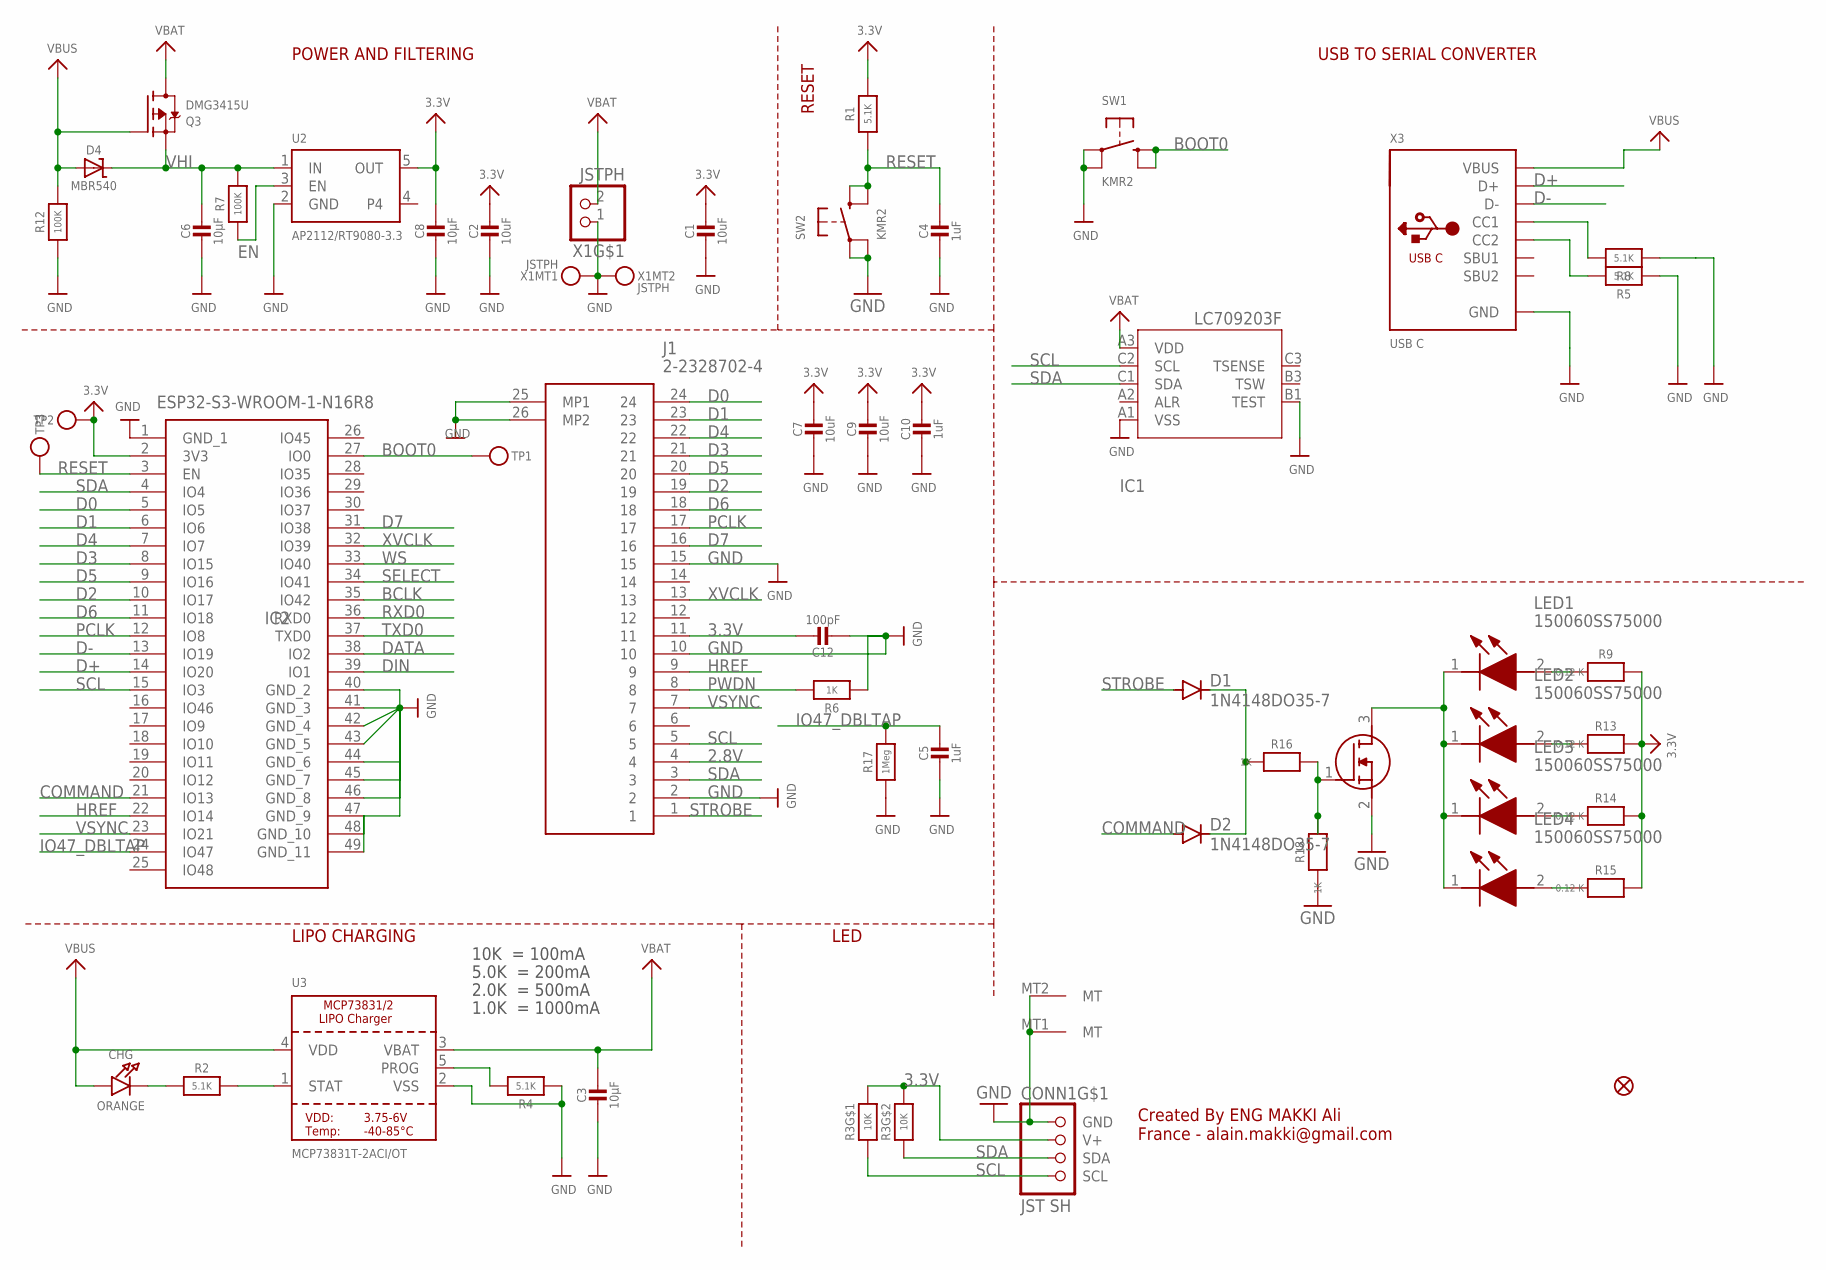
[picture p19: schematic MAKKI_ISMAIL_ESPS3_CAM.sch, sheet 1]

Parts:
C1, C2, C7, C9: 10uF; 0805-NO
C3, C6, C8: 10µF; 0805-NO
C4, C5, C10: 1uF; 0603-NO
C12: 100pF; 0805-NO
CHG: ORANGE; CHIPLED_0603_NOOUTLINE
CONN1: JST SH; JST_SH4_RA
D1, D2: 1N4148DO35-7; DO35-7
D4: MBR540; SOD-123
IC1: LC709203F/MH; WLCSP9
IC2: ESP32-S3-WROOM-1-N16R8; ESP32S3WROOM1N16R8
J1: 2-2328702-4; 223287024
LED1, LED2, LED3, LED4: 150060SS75000; LEDC1608X80N
Q2: 2N7002; SOT96P240X120-3N
Q3: DMG3415U; SOT23-R
R1, R2, R4, R5, R8: 5.1K; 0603-NO
R3: 10K; RESPACK_4X0603
R6, R16, R18: 1K; 0603-NO
R7, R12: 100K; 0603-NO
R9, R13, R14, R15: 0.12 K; 0603-NO
R17: 1Meg; 0603-NO
SW1, SW2: KMR2; BTN_KMR2_4.6X2.8
TP1, TP2, TP3: TESTPOINTROUND1.5MMNO; TESTPOINT_ROUND_1.5MM_NO
U2: AP2112/RT9080-3.3; SOT23-5
U3: MCP73831T-2ACI/OT; SOT23-5
U$34: FIDUCIAL_1MM
X1: JSTPH; JSTPH2_BATT
X3: USB C; USB_C_CUSB31-CFM2AX-01-X

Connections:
2.8V: J1.4; also elsewhere on the board
3.3V: C1.1, C2.1, C7.1, C8.1, C9.1, C10.1, C12.1, CONN1.2 (V+), IC2.2 (3V3), J1.11, R1.2, R3.7 (2), R3.8 (2), R9.2, R13.2, R14.2, R15.2, TP2.P$1, U2.5 (OUT); also elsewhere on the board
BCLK: IC2.35 (IO42); also elsewhere on the board
BOOT0: IC2.27 (IO0), SW1.B (S), SW1.B' (S1), TP1.P$1
COMMAND: D2.A, IC2.21 (IO13)
D0: IC2.5 (IO5), J1.24
D1: IC2.6 (IO6), J1.23
D2: IC2.10 (IO17), J1.19
D3: IC2.8 (IO15), J1.21
D4: IC2.7 (IO7), J1.22
D5: IC2.9 (IO16), J1.20
D6: IC2.11 (IO18), J1.18
D7: IC2.31 (IO38), J1.16
D+: IC2.14 (IO20), X3.A6 (D+), X3.B6 (D+)
D-: IC2.13 (IO19), X3.A7 (D-), X3.B7 (D-)
DATA: IC2.38 (IO2); also elsewhere on the board
DIN: IC2.39 (IO1); also elsewhere on the board
EN: R7.1, U2.3 (EN)
GND: C1.2, C2.2, C3.2, C4.2, C5.2, C6.2, C7.2, C8.2, C9.2, C10.2, C12.2, CONN1.1 (GND), CONN1.MT1 (MT), CONN1.MT2 (MT), IC1.A1 (VSS), IC1.B1 (TEST), IC2.1 (GND_1), IC2.40 (GND_2), IC2.41 (GND_3), IC2.42 (GND_4), IC2.43 (GND_5), IC2.44 (GND_6), IC2.45 (GND_7), IC2.46 (GND_8), IC2.47 (GND_9), IC2.48 (GND_10), IC2.49 (GND_11), J1.2, J1.10, J1.15, J1.25 (MP1), J1.26 (MP2), Q2.2 (S), R4.1, R5.1, R6.1, R8.1, R12.1, R17.1, R18.1, SW1.A, SW1.A' (P1), SW2.A, SW2.A' (P1), U2.2 (GND), U3.2 (VSS), X1.1, X1.NC1, X1.NC2, X3.A1B12 (GND), X3.B1A12 (GND); also elsewhere on the board
HREF: IC2.22 (IO14), J1.9
IO47_DBLTAP: C5.1, IC2.24 (IO47), R17.2
unnamed: CHG.C, R2.1
unnamed: LED1.2 (A), R9.1
unnamed: R2.2, U3.1 (STAT)
unnamed: R4.2, U3.5 (PROG)
unnamed: R8.2, X3.A5 (CC1)
unnamed: R5.2, X3.B5 (CC2)
unnamed: LED2.2 (A), R13.1
unnamed: LED3.2 (A), R14.1
unnamed: LED4.2 (A), R15.1
unnamed: LED1.1 (K), LED2.1 (K), LED3.1 (K), LED4.1 (K), Q2.3 (D)
unnamed: D1.C, D2.C, R16.1
unnamed: Q2.1 (G), R16.2, R18.2
PCLK: IC2.12 (IO8), J1.17
PWDN: J1.8, R6.2
RESET: C4.1, IC2.3 (EN), R1.1, SW2.B (S), SW2.B' (S1), TP3.P$1
RXD0: IC2.36 (RXD0)
SCL: CONN1.4 (SCL), IC1.C2 (SCL), IC2.15 (IO3), J1.5, R3.1
SDA: CONN1.3 (SDA), IC1.C1 (SDA), IC2.4 (IO4), J1.3, R3.2 (1)
SELECT: IC2.34 (IO41); also elsewhere on the board
STROBE: D1.A, J1.1
TXD0: IC2.37 (TXD0)
VBAT: C3.1, IC1.A3 (VDD), Q3.3 (D), U3.3 (VBAT), X1.2
VBUS: CHG.A, D4.A, Q3.1 (G), R12.2, U3.4 (VDD), X3.A4B9 (VBUS), X3.B4A9 (VBUS)
VHI: C6.1, D4.C, Q3.2 (S), R7.2, U2.1 (IN)
VSYNC: IC2.23 (IO21), J1.7
WS: IC2.33 (IO40); also elsewhere on the board
XVCLK: IC2.32 (IO39), J1.13

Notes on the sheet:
POWER AND FILTERING
RESET
10K = 100mA
5.0K = 200mA
2.0K = 500mA
1.0K = 1000mA
USB TO SERIAL CONVERTER
LIPO CHARGING
LED
Created By ENG MAKKI Ali France - alain.makki@gmail.com

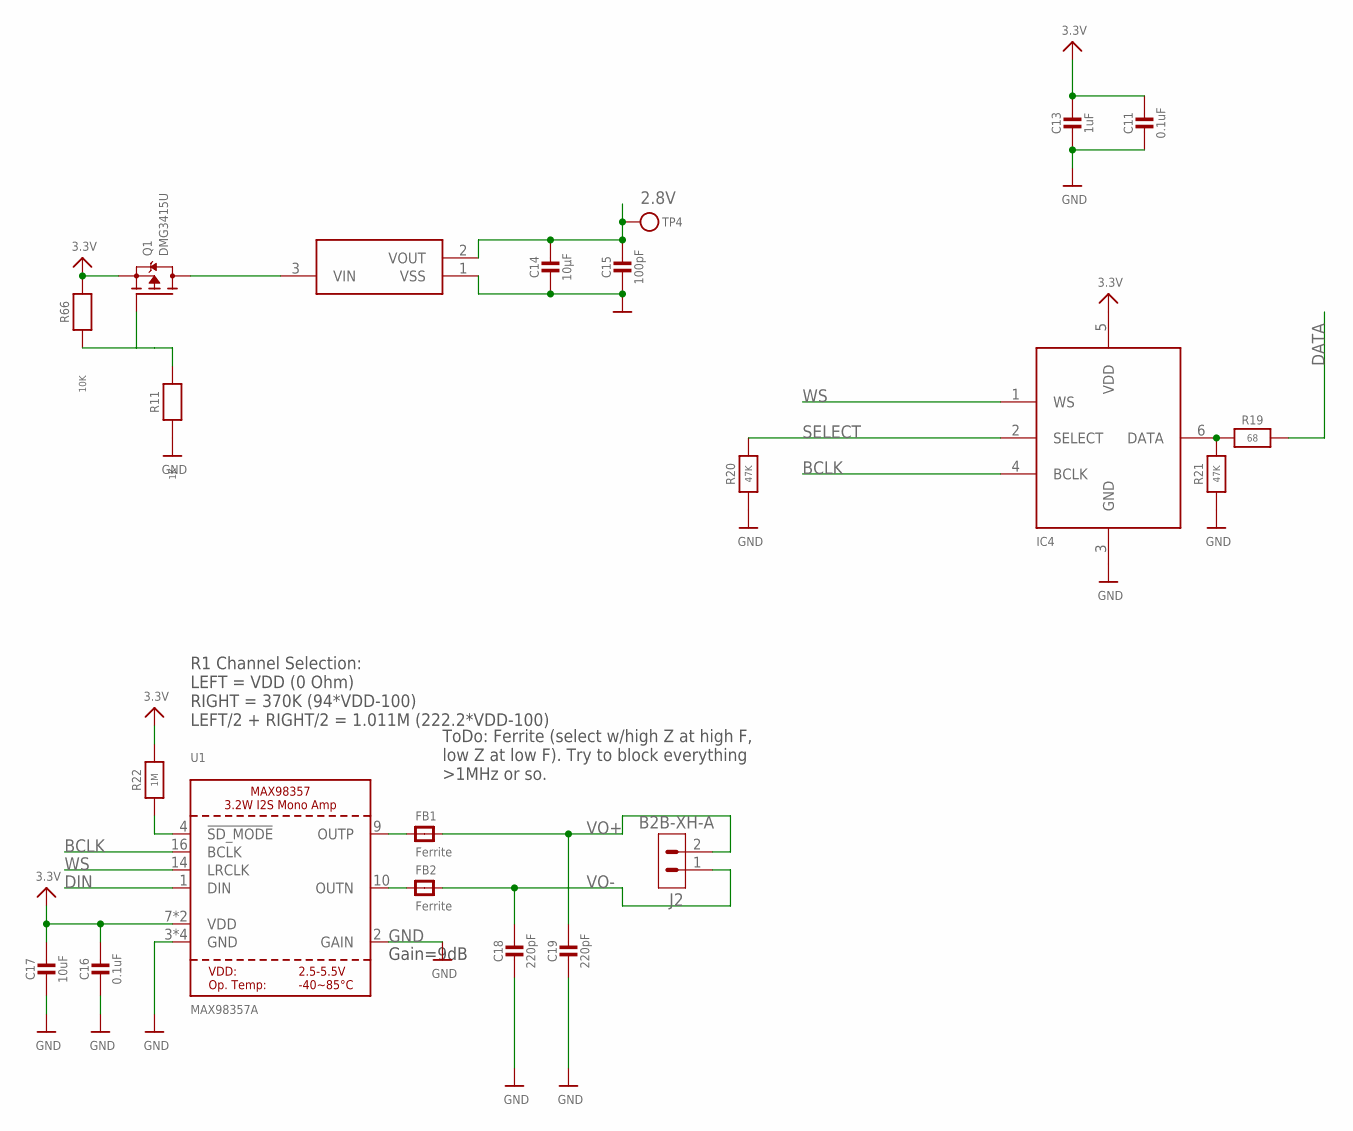
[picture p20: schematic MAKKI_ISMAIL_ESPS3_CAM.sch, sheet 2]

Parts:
C11: 0.1uF; 0603-NO
C13: 1uF; 0603-NO
C14: 10µF; 0805-NO
C15: 100pF; 0805-NO
C16: 0.1uF; 0805-NO
C17: 10uF; 0805-NO
C18, C19: 220pF; 0805-NO
FB1, FB2: Ferrite; 0805-NO
IC3: XC6206P282MR-G; SOT95P280X130-3N
IC4: ICS-43434; SPH0645LM4H
J2: B2B-XH-A
Q1: DMG3415U; SOT23-R
R11: 1K; 0603-NO
R19: 68; 0603-NO
R20, R21: 47K; 0603-NO
R22: 1M; 0805-NO
R66: 10K; 0603-NO
TP4: TESTPOINTROUND1.5MMNO; TESTPOINT_ROUND_1.5MM_NO
U1: MAX98357A; QFN16_3MM

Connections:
2.8V: C14.1, C15.1, IC3.2 (VOUT), TP4.P$1; also elsewhere on the board
3.3V: C11.1, C13.1, C16.1, C17.1, IC4.5 (VDD), Q1.2 (S), R22.2, R66.2, U1.7 (VDD), U1.8 (VDD); also elsewhere on the board
BCLK: IC4.4 (BCLK), U1.16 (BCLK); also elsewhere on the board
DATA: R19.2; also elsewhere on the board
DIN: U1.1 (DIN); also elsewhere on the board
GND: C11.2, C13.2, C14.2, C15.2, C16.2, C17.2, C18.2, C19.2, IC3.1 (VSS), IC4.3 (GND), R11.1, R20.1, R21.1, U1.2 (GAIN), U1.3 (GND), U1.11 (GND), U1.15 (GND), U1.THERMAL (GND); also elsewhere on the board
unnamed: Q1.1 (G), R11.2, R66.1
unnamed: IC3.3 (VIN), Q1.3 (D)
unnamed: IC4.6 (DATA), R19.1, R21.2
unnamed: FB2.1, U1.10 (OUTN)
unnamed: FB1.1, U1.9 (OUTP)
SD_MODE: R22.1, U1.4 (!SD_MODE)
SELECT: IC4.2 (SELECT), R20.2; also elsewhere on the board
VO+: C19.1, FB1.2, J2.2
VO-: C18.1, FB2.2, J2.1
WS: IC4.1 (WS), U1.14 (LRCLK); also elsewhere on the board

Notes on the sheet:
R1 Channel Selection: LEFT = VDD (0 Ohm) RIGHT = 370K (94*VDD-100) LEFT/2 + RIGHT/2 = 1.011M (222.2*VDD-100)
ToDo: Ferrite (select w/high Z at high F, low Z at low F). Try to block everything >1MHz or so.
Gain=9dB

Board: 2 copper layers, 74 parts (8 on the bottom side), 54 nets, no tracks yet.

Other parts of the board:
U$35: FIDUCIAL_1MM

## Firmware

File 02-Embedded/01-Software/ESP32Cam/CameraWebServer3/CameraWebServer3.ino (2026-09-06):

#include "esp_camera.h"
#include <WiFi.h>
#include <WebServer.h>

#define CAMERA_MODEL_AI_THINKER

#include "camera_pins.h"

const char* ssid = "****"; // Remplacez par votre SSID WiFi
const char* password = "****"; // Remplacez par votre mot de passe WiFi

WebServer server(80);

void handleRoot() {
  server.send(200, "text/plain", "Hello, this is ESP32-CAM");
}

void handleCapture() {
  camera_fb_t * fb = NULL;
  fb = esp_camera_fb_get();
  if (!fb) {
    Serial.println("Camera capture failed");
    server.send(500, "text/plain", "Camera capture failed");
    return;
  }

  Serial.println("Camera capture succeeded");

  WiFiClient client = server.client();

  client.println("HTTP/1.1 200 OK");
  client.println("Content-Type: image/jpeg");
  client.print("Content-Length: ");
  client.println(fb->len);
  client.println();
  client.write(fb->buf, fb->len);

  esp_camera_fb_return(fb);
}

void setup() {
  Serial.begin(115200);
  Serial.setDebugOutput(true);
  Serial.println();

  // Configuration de la caméra
  camera_config_t config;
  config.ledc_channel = LEDC_CHANNEL_0;
  config.ledc_timer = LEDC_TIMER_0;
  config.pin_d0 = Y2_GPIO_NUM;
  config.pin_d1 = Y3_GPIO_NUM;
  config.pin_d2 = Y4_GPIO_NUM;
  config.pin_d3 = Y5_GPIO_NUM;
  config.pin_d4 = Y6_GPIO_NUM;
  config.pin_d5 = Y7_GPIO_NUM;
  config.pin_d6 = Y8_GPIO_NUM;
  config.pin_d7 = Y9_GPIO_NUM;
  config.pin_xclk = XCLK_GPIO_NUM;
  config.pin_pclk = PCLK_GPIO_NUM;
  config.pin_vsync = VSYNC_GPIO_NUM;
  config.pin_href = HREF_GPIO_NUM;
  config.pin_sscb_sda = SIOD_GPIO_NUM;
  config.pin_sscb_scl = SIOC_GPIO_NUM;
  config.pin_pwdn = PWDN_GPIO_NUM;
  config.pin_reset = RESET_GPIO_NUM;
  config.xclk_freq_hz = 20000000;
  config.pixel_format = PIXFORMAT_JPEG;

  if (psramFound()) {
    config.frame_size = FRAMESIZE_SVGA;
    config.jpeg_quality = 2;
    config.fb_count = 2;
  } else {
    config.frame_size = FRAMESIZE_SVGA;
    config.jpeg_quality = 2;
    config.fb_count = 1;
  }

  esp_err_t err = esp_camera_init(&config);
  if (err != ESP_OK) {
    Serial.printf("Camera init failed with error 0x%x", err);
    return;
  }

  WiFi.begin(ssid, password);

  while (WiFi.status() != WL_CONNECTED) {
    delay(500);
    Serial.print(".");
  }
  Serial.println("");
  Serial.println("WiFi connected");

  Serial.print("Camera Ready! Use 'http://");
  Serial.print(WiFi.localIP());
  Serial.println("' to connect");

  server.on("/", HTTP_GET, handleRoot);
  server.on("/capture", HTTP_GET, handleCapture);
  server.begin();
}

void loop() {
  server.handleClient();
}

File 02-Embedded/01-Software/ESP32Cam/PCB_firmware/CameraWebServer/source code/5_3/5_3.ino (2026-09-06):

#include "esp_camera.h"
#include <WiFi.h>
#include <Preferences.h>

#define PWDN_GPIO_NUM     -1
#define RESET_GPIO_NUM    -1
#define XCLK_GPIO_NUM     11
#define Y9_GPIO_NUM 5  //done
#define Y8_GPIO_NUM 6 //done
#define Y7_GPIO_NUM 7 //done
#define Y6_GPIO_NUM 15 //done
#define Y5_GPIO_NUM 16 //done
#define Y4_GPIO_NUM 17 //done
#define Y3_GPIO_NUM 18 //done
#define Y2_GPIO_NUM 9 //done
#define VSYNC_GPIO_NUM    21
#define HREF_GPIO_NUM     14
#define PCLK_GPIO_NUM     8
#define SIOD_GPIO_NUM 4 //done
#define SIOC_GPIO_NUM 3 //done


Preferences preferences;
const char* ssid;
const char* password;

void startCameraServer();
void setupLedFlash(int pin);

void connectToWiFi(const char* ssid, const char* password) {
  WiFi.begin(ssid, password);
  Serial.printf("Connecting to WiFi: %s\n", ssid);
  int retries = 0;
  while (WiFi.status() != WL_CONNECTED && retries < 20) {
    delay(500);
    Serial.print(".");
    retries++;
  }

  if (WiFi.status() == WL_CONNECTED) {
    Serial.println("\nWiFi connected!");
    Serial.print("IP address: ");
    Serial.println(WiFi.localIP());
  } else {
    Serial.println("\nFailed to connect to WiFi.");
  }
}

void initWiFi() {
  preferences.begin("wifi", false);
  String savedSSID = preferences.getString("ssid", "hassan");
  String savedPASS = preferences.getString("password", "12345678");

  if (savedSSID.length() > 0 && savedPASS.length() > 0) {
    Serial.println("Found saved WiFi credentials.");
    connectToWiFi(savedSSID.c_str(), savedPASS.c_str());

    if (WiFi.status() == WL_CONNECTED) {
      return;
    } else {
      Serial.println("Stored credentials failed. Please enter new credentials.");
    }
  } else {
    Serial.println("No WiFi credentials found. Please enter:");
  }

  while (Serial.available()) Serial.read();

  Serial.println("Enter SSID: ");
  while (Serial.available() == 0) delay(10);
  String inputSSID = Serial.readStringUntil('\n');
  inputSSID.trim();

  Serial.println("Enter Password: ");
  while (Serial.available() == 0) delay(10);
  String inputPASS = Serial.readStringUntil('\n');
  inputPASS.trim();

  connectToWiFi(inputSSID.c_str(), inputPASS.c_str());

  if (WiFi.status() == WL_CONNECTED) {
    preferences.putString("ssid", inputSSID);
    preferences.putString("password", inputPASS);
    Serial.println("WiFi credentials saved.");
  } else {
    Serial.println("Failed to connect. Credentials not saved.");
  }

  preferences.end();
}

void initCamera(){
  camera_config_t config;
  config.ledc_channel = LEDC_CHANNEL_0;
  config.ledc_timer = LEDC_TIMER_0;
  config.pin_d0 = Y2_GPIO_NUM;
  config.pin_d1 = Y3_GPIO_NUM;
  config.pin_d2 = Y4_GPIO_NUM;
  config.pin_d3 = Y5_GPIO_NUM;
  config.pin_d4 = Y6_GPIO_NUM;
  config.pin_d5 = Y7_GPIO_NUM;
  config.pin_d6 = Y8_GPIO_NUM;
  config.pin_d7 = Y9_GPIO_NUM;
  config.pin_xclk = XCLK_GPIO_NUM;
  config.pin_pclk = PCLK_GPIO_NUM;
  config.pin_vsync = VSYNC_GPIO_NUM;
  config.pin_href = HREF_GPIO_NUM;
  config.pin_sccb_sda = SIOD_GPIO_NUM;
  config.pin_sccb_scl = SIOC_GPIO_NUM;
  config.pin_pwdn = PWDN_GPIO_NUM;
  config.pin_reset = RESET_GPIO_NUM;
  config.xclk_freq_hz = 20000000;
  config.frame_size = FRAMESIZE_UXGA;
  config.pixel_format = PIXFORMAT_JPEG;  // for streaming
  //config.pixel_format = PIXFORMAT_RGB565; // for face detection/recognition
  config.grab_mode = CAMERA_GRAB_WHEN_EMPTY;
  config.fb_location = CAMERA_FB_IN_PSRAM;
  config.jpeg_quality = 12;
  config.fb_count = 1;

  // if PSRAM IC present, init with UXGA resolution and higher JPEG quality
  //                      for larger pre-allocated frame buffer.
  if (config.pixel_format == PIXFORMAT_JPEG) {
    if (psramFound()) {
      config.jpeg_quality = 10;
      config.fb_count = 2;
      config.grab_mode = CAMERA_GRAB_LATEST;
    } else {
      // Limit the frame size when PSRAM is not available
      config.frame_size = FRAMESIZE_SVGA;
      config.fb_location = CAMERA_FB_IN_DRAM;
    }
  } else {
    // Best option for face detection/recognition
    config.frame_size = FRAMESIZE_240X240;
  }

  // camera init
  esp_err_t err = esp_camera_init(&config);
  if (err != ESP_OK) {
    Serial.printf("Camera init failed with error 0x%x", err);
    return;
  }

  sensor_t *s = esp_camera_sensor_get();
  // initial sensors are flipped vertically and colors are a bit saturated
  if (s->id.PID == OV3660_PID) {
    s->set_vflip(s, 1);        // flip it back
    s->set_brightness(s, 1);   // up the brightness just a bit
    s->set_saturation(s, -2);  // lower the saturation
  }
  // drop down frame size for higher initial frame rate
  if (config.pixel_format == PIXFORMAT_JPEG) {
    s->set_framesize(s, FRAMESIZE_QVGA);
  }
}



void setup() {
  Serial.begin(115200);
  Serial.setDebugOutput(true);
  delay(1000);
  Serial.println();
  
  initCamera();
  initWiFi();
  startCameraServer();
}

void loop() {
  // Do nothing. Everything is done in another task by the web server
  delay(10000);
}

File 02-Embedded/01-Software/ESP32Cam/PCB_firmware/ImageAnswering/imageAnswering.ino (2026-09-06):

#include <WiFi.h>
#include <OpenAI.h>
#include "camera.h"
#include "wav_header.h"
#include <Arduino.h>
#include <SPI.h>
#include "FS.h"
#include "SD.h"
#include "SPI.h"
#include "ESP_I2S.h"
#define BUTTON_PIN 0
#define SAMPLE_RATE     (16000)
#define DATA_PIN        (GPIO_NUM_4)
#define CLOCK_PIN       (GPIO_NUM_3)


const char* ssid = "Fatima";
const char* password = "123123123";
const char* api_key = "";

OpenAI openai(api_key);
OpenAI_ChatCompletion chat(openai);
OpenAI_AudioTranscription audio(openai);
OpenAI_TTS tts(openai);
I2SClass I2S;
bool isRecording = false; 
uint8_t *wavBuffer = NULL;
size_t wavBufferSize = 0; 

void setup(){
  Serial.begin(115200);
  pinMode(BUTTON_PIN, INPUT_PULLUP);
  audioInit();
  initCamera();
  WiFi.begin(ssid, password);
  Serial.print("Connecting");
  while (WiFi.status() != WL_CONNECTED) { 
    delay(100);
    Serial.print(".");
  }
  Serial.println("success!");
  chatInit();
}
void loop() {
    if (digitalRead(BUTTON_PIN) == LOW) {
        if (!isRecording) {
            startRecording();
        }
    } else {
        if (isRecording) {
            stopRecording();
        }
    }
    if (isRecording) {
        size_t bytesAvailable = I2S.available();
        if (bytesAvailable > 0) {
            uint8_t *newBuffer = (uint8_t *)realloc(wavBuffer, wavBufferSize + bytesAvailable);
            if (newBuffer == NULL) {
                log_e("Failed to reallocate WAV buffer");
                stopRecording();
                return;
            }
            wavBuffer = newBuffer;

            size_t bytesRead = I2S.readBytes((char *)(wavBuffer + wavBufferSize), bytesAvailable);
            wavBufferSize += bytesRead;
        }
    }

    delay(10); 
}
void audioInit()
{
  I2S.setPinsPdmRx(CLOCK_PIN, DATA_PIN);
  if (!I2S.begin(I2S_MODE_PDM_RX, SAMPLE_RATE, I2S_DATA_BIT_WIDTH_16BIT, I2S_SLOT_MODE_MONO)) {
    Serial.println("Failed to initialize I2S PDM RX");
  }
}
void chatInit()
{
  chat.setModel("gpt-4o-mini");   //Model to use for completion. Default is gpt-4-vision-preview is needed for image analysis
  chat.setSystem("Code geek");      //Description of the required assistant
  chat.setMaxTokens(1000);          //The maximum number of tokens to generate in the completion.
  chat.setTemperature(0.2);         //float between 0 and 2. Higher value gives more random results.
  chat.setStop("\r");               //Up to 4 sequences where the API will stop generating further tokens.
  chat.setPresencePenalty(0);       //float between -2.0 and 2.0. Positive values increase the model's likelihood to talk about new topics.
  chat.setFrequencyPenalty(0);      //float between -2.0 and 2.0. Positive values decrease the model's likelihood to repeat the same line verbatim.
  chat.setUser("OpenAI-ESP32-cam");     //A unique identifier representing your end-user, which can help OpenAI to monitor and detect abuse.
}

String SpeechToText()
{
  String  txt = audio.file(wavBuffer,wavBufferSize,(OpenAI_Audio_Input_Format)5);
  free(wavBuffer);
  wavBuffer = NULL;
  wavBufferSize = 0;
  return txt;
}

String imageAnswering(String txt)
{
  camera_fb_t *fb = NULL; 
  String response;
  // Take Picture with Camera and return pointer to image buffer
  fb = esp_camera_fb_get();
  Serial.println("capuring image");
  delay(5);
  esp_camera_fb_return(fb);
  delay(1000);
  Serial.println("sending image to openai");
  OpenAI_StringResponse result = chat.message(txt,fb->buf,fb->len); // enter your prompt with the image buffer and the length of the buffer

  if(result.length() >= 1){
    for (unsigned int i = 0; i < result.length(); ++i){
      response = result.getAt(i);
      response.trim();
    }
  }
  return response;
}

int TextToSpeech(String txt)
{
  return tts.message(txt);
}

void startRecording() {
    size_t sampleRate = I2S.rxSampleRate();
    uint16_t sampleWidth = (uint16_t)I2S.rxDataWidth();
    uint16_t numChannels = (uint16_t)I2S.rxSlotMode();

    wavBufferSize = 0;
    wavBuffer = (uint8_t *)malloc(PCM_WAV_HEADER_SIZE);
    if (wavBuffer == NULL) {
        log_e("Failed to allocate WAV buffer");
        return;
    }

    const pcm_wav_header_t wavHeader = PCM_WAV_HEADER_DEFAULT(0, sampleWidth, sampleRate, numChannels);
    memcpy(wavBuffer, &wavHeader, PCM_WAV_HEADER_SIZE);
    wavBufferSize = PCM_WAV_HEADER_SIZE;

    Serial.println("Start recording...");
    isRecording = true;
}

void stopRecording() {
    if (!isRecording) return;

    isRecording = false;
    Serial.printf("Stop recording. Total recorded size: %u\n", wavBufferSize);

    pcm_wav_header_t *header = (pcm_wav_header_t *)wavBuffer;
    header->descriptor_chunk.chunk_size =  (wavBufferSize) + sizeof(pcm_wav_header_t) - 8;
    header->data_chunk.subchunk_size = wavBufferSize - PCM_WAV_HEADER_SIZE;

    Serial.println("Start speech to text! ");
    String txt = SpeechToText();
    if(txt!=NULL){
        Serial.printf("SpeechToText Message:\n%s\n", txt.c_str());
        Serial.println("Start image Answering! ");
        txt=imageAnswering(txt);
        if(txt!=NULL){
          Serial.printf("imageAnswering Message:\n%s\n", txt.c_str());
          Serial.println("Start text to audio! ");
          if(TextToSpeech(txt)==-1){
            Serial.println("Audio reception failed! ");
          }
        }else{
          Serial.println("imageAnswering failed!");
        }
    }else{
      Serial.println("speech to text failed!");
    }
}

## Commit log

2024-11-25 Ajout du fichier d'entrainement, ainsi que du modèle yolov5 avec pyTorch
2024-11-27 Ajout de l'affichage des résultats
2024-11-28 creation des fichier de dataset
2024-12-08 Initial glasses model
    [Pièce1.SLDPRT]
2024-12-16 impression une camera
    [Assemblage_lunettes - Boitier-2.STL, Assemblage_lunettes - Lunettes-1.STL, Assemblage_lunettes.SLDASM, Boitier.SLDPRT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]
2024-12-19 Entrainement yolov11 avec 3 version :: Nano Small et Medium
    [results.csv]
2025-01-23 Ajout du dossier wifi_mode_switch_proj avec les fichiers de configuration
2025-02-07 all previous commit
    [results.csv]
2025-02-18 Fichier avec tts, et affichage de la date et l'heure
2025-10-31 Update file organization
    [data.xlsx]
2026-02-11 PCB_firmware added
2026-02-11 CameraWebS et Yolo
    [partitions.csv]
2026-02-11 Add Hardware design
    [Adafruit ESP32-S3 8MB No PSRAM.brd, Adafruit ESP32-S3 8MB No PSRAM.sch, MAKKI_ISMAIL_ESPS3_CAM.PcbDoc, MAKKI_ISMAIL_ESPS3_CAM.PrjPcb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]
2026-02-13 Version Corrige
    [MAKKI_ISMAIL_ESPS3_CAM.PcbDoc, MAKKI_ISMAIL_ESPS3_CAM.PrjPcb, MAKKI_ISMAIL_ESPS3_CAM.sch, MAKKI_ISMAIL_ESPS3_CAM_0.SchDoc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]

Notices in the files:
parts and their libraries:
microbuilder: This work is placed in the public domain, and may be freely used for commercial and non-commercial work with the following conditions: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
